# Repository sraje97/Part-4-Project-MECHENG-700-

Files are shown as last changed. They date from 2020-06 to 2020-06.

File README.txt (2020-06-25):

MECHENG700 - P4P
Eye-tracking System for Diagnosis of Visual Deficits
Author: S. Raje & J. Zhang

This contains all the MATLAB files used throughout the Part 4 project.
The files include:
	- On screen stimulus visualisation
	- Calibration Test
	- Fixation Tests
	- Trajectory Tests
	- Analyses for each test (Fourier analysis, Gaze position, Calibration, etc.)

The folder also includes a subfolder, "FINAL", of a few subject's results following the tests.

The final report and presentation are shown in the pdf and powerpoint slides respectively.

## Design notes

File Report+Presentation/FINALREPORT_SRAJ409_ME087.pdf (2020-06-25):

EYE-TRACKING SYSTEM FOR DIAGNOSIS OF VISUAL DEFICITS

### Sidhant Raje

Project Report ME087-2019

### RESEARCH PROJECT IN MECHATRONICS ENGINEERING

Co-worker: Jerry (Jia Jun) Zhang

Supervisor: Dr Luke Hallum

Department of Mechanical Engineering The University of Auckland

27 September 2019

ME087-2019

### EYE TRACKING SYSTEM FOR DIAGNOSIS OF VISUAL DEFICITS

### Sidhant Raje

### ABSTRACT

Millions of adults and children around the world suffer from visual deficits. When left untreated these visual deficits can cause severe vision loss and psychosocial issues [1]. This study pursues the design, build, and testing of an eye-tracking system for the diagnosis of strabismus, allowing for successful classifying and quantifying of strabismus.
The trials include a head mounted eye-tracker (the Jazz-novo), a CRT monitor, and dichroic filters (red and blue) for dichoptic presentation. Two sets of tests were carried out; firstly the 9-point fixation test, then the smooth pursuit tracking test. The visual stimuli was presented dichoptically such that at any one time, monocular perception was engaged whilst fixating or tracking. The stimuli was a circular, blue or red point which was only perceived through the right colour filter (blue for blue, red for red).
The fixation test stimulus oscillated 10 times (blue and red) with a frequency of 1 HZ at each of the nine locations on the grid. The tracking test stimulus travelled across both the horizontal and vertical meridians twice (once with blue stimulus and once with red stimulus). The tracking motion was a sinusoidal function, with a frequency of 0.12 Hz. Eight subjects participated in the formal trials of this experiment. Fast Fourier Transform (FFT) analyses were computed on the data from these subjects to acquire amplitudes, gains, and phases for the different sets of tests.
Results in this report outline two subjects who showed interesting results, one for fixation and one for tracking, and separate group analyses were also carried out. The results revealed distinct oscillations in the 1 Hz component of the eye-tracking data in either X or Y displacement for the fixation test. These amplitudes were compared relative to each subject’s calibration point and a relative gain was established for each subject. A larger gain meant larger magnitude of deviations which led to potential signs of strabismus. The tracking test results portrayed the gain and phase of the subject’s ability to track a moving stimuli. Higher gains meant there were overshoots from the relative gaze position, whilst lower gain corresponded to undershoots. Group results for the difference between Dominant Eye (DE) and Non-dominant Eye (NDE) gains and phases were also retrieved which revealed a possibility of diagnosing strabismus.
The results open an opportunity to diagnose and quantify strabismus with improving eye-tracking technology. These could one day lead to mobile eye-tracking systems in clinical practices for efficient use of time, resources, and introduce a level of autonomy.

ii

DECLARATION

Student

I hereby declare that:

1. This report is the result of the final year project work carried out by my project partner (see cover page) and I under the guidance of our supervisor (see cover page) in the 2019 academic year at the Department of Mechanical Engineering, Faculty of Engineering, University of Auckland.
2. This report is not the outcome of work done previously.
3. This report is not the outcome of work done in collaboration, except that with a potential project sponsor (if any) as stated in the text.
4. This report is not the same as any report, thesis, conference article or journal paper, or any other publication or unpublished work in any format.

In the case of a continuing project, please state clearly what has been developed during the project and what was available from previous year(s):

Signature:

Date:

Supervisor

I confirm that the project work undertaken by this student in the 2019 academic year is / is not (strikethrough as appropriate) part of a continuing project, components of which have been completed previously. Comments, if any:

Signature:

Date:

iii

### Table of Contents

iv

### List of Figures

Figure 1 | Four types of strabismic deviations | | 2
Figure 2 | Example of Prism-Cover test and the signs of esotropic strabismus . | 3
Figure 3 | Overview of eye-tracking system setup | | 6
Figure 4 | a) Chinrest and dichroic filter setup for subject. b) Subject performing
fixation test. c) Subject wearing the Jazz-novo eye-tracker | | 7
Figure 5 | Fixation and tracking test stimuli layout. a) 4-point calibration for
fixation test. b) Fixation test layout. c) Two 2-point calibration for tracking
test. d) Tracking test layout | | 9
Figure 6 | Subject testing procedure flow diagram | 10
Figure 7 | Data acquisition methodology | 11
Figure 8 | Subject A fixation test with filter placement RB. a) XY plot of the
9-point fixation test. b) X and Y displacement against time for fixation point 6. c) FFT analysis of X position at fixation point 6. d) FFT analysis
of Y position at fixation point 6 | 13
Figure 9 Overlay of normalised Y position for filter placements RB and BR at
fixation point 6 | 14
Figure 10 Fixation amplitude at 1 Hz over calibration amplitude at 1 Hz at the bottom-left corner of 9-point grid. a) Relative horizontal gain for all 8
subjects. b) Relative vertical gain for all 8 subjects | 15
Figure 11 Subject B tracking test response with filter placement RB. a) Horizontal tracking with left eye. b) Horizontal tracking with right eye. c)
Vertical tracking with left eye. d) Vertical tracking with right eye | 16
Figure 12 Polar plot of gain and phase for horizontal tracking. a) Dominant eye tracking. b) Non-dominant eye tracking. c) Difference between dominant
and non-dominant eye | 17
Figure 13 Polar plot of gain and phase for vertical tracking. a) Dominant eye tracking. b) Non-dominant eye tracking. c) Difference between dominant
and non-dominant eye | 18

### List of Tables

Table 1 | Subject information | 12
Table 2 | Subject B Gain and Phase at 0.12 Hz component | 16

v

### Acknowledgements

I would like to take this opportunity to thank the many people involved directly or indirectly with this project and those who have supported me in any way big or small throughout the year.
Firstly, I would like to thank my project partner, Jerry Zhang, for his consistent hard work and dedication to this research project. His passion for this research area kept me motivated throughout the year and contributed greatly to the success of this project. I could not have asked for a better peer to work alongside with.
I would like to thank our supervisor, Dr. Luke Hallum, for going above and beyond with his continuous support and guidance. His expertise and advice always came in handy whenever we hit a roadblock and his feedback throughout the various stages of this project are greatly appreciated. He has inspired me to follow this field of research in my forthcoming years.
I would also like to thank Lucy Yan for her support throughout the year. She has always been there to talk to for any of our hurdles and provided excellent ideas and solutions to overcome them.
Finally, I would like to thank our friends, family, and peers who dedicated their precious time for our experimental trials. There efforts are acknowledged and contributed greatly to the success of this project.

vi

### Glossary of Terms

Visual Deficit | Visual impairments leading to decreased vision
Eye Tracking | Measurements denoting the horizontal and vertical positions of
| a subject’s gaze
Dichoptic Presentation Presenting a stimulus to one eye at a time
Monocular Perception Seeing the visual stimulus through a single eye
Binocular Perception Seeing the visual stimulus via both eyes simultaneously

### Abbreviations

VA | Visual Acuity
ADC | Analogue to Digital Converter
FFT | Fast Fourier Transform
DE | Dominant Eye
NDE | Non-dominant Eye

vii

### 1. Introduction

Millions of adults and children around the world suffer from visual deficits. When left untreated these can cause severe vision loss and psychosocial issues [1]. Adverse psychosocial effects consist of problems in childhood and education, job prospects, interaction with peers, may manifest more seriously as psychiatric disorders, and may also be detrimental to the general quality of life [2]. According to the American Academy of Pediatrics, early diagnosis and intervention is necessary in preschool and early childhood to reduce these risks by more than 50%, by the age of 7. Children with first-degree relatives with similar conditions should also be referred to testings early on [3].
There are many shortcomings to the manual visual diagnostic methods currently in use. Majority of the current visual diagnostic methods require a professional or specialist to conduct the vision screening tests. These are manual and lack quantitative measures. They use resources and time from the facility as well as the patients, making them expensive and undesirable. Furthermore, the conducting of the screening tests is often difficult and subjective, and predominantly requires communication between the patient and ophthalmologist. This can lead to a communication barrier with young or non-verbal children. In these cases specifically, observational methods are favourable and should be conducted. Eye-tracking is a non-invasive method currently used for detecting visual abnormalities in patients. Eye-tracking is a relatively new area of research but becoming increasingly popular as technology advancements occur with cheaper, more reliable eye-trackers being more readily available - thanks to the gaming industry. These new devices can slowly minimise the subjectivity of tests and bring in more accurate measurements. There are multiple areas in life where research is being done using eye-tracking devices including; medical research, marketing and social applications, education, and gaming/VR [4]. In this paper, we focus on the medical research and usage of eye-trackers; specifically, the diagnosis of visual deficits using an eye-tracking system.
We propose to develop a test for diagnosing strabismus using eye-tracking. Our test must, for the most part, be automatic and objective when detecting strabismus in subjects. We will acquire gaze position using fixation points for the subject to observe on screen, and a set of horizontal and vertical traversals to track. Through our trials and testing, the data gathered and analysed should give us a better understanding of visual acuity in strabismic subjects and potentially lead to developing a quick-and-easy, mobile system for use by ophthalmologists or paediatricians in visual screening tests.

### 2. Literature Review

### 2.1 Visual Deficits

There are a number of visual deficits which affect visual acuity and many of these can have potentially adverse effects on the patient. Strabismus is one of the most commonly diagnosed visual abnormalities which could lead to visual deficits. Fortunately, treatment of strabismus has high success rate if treated early. Therefore, we are focusing our study on diagnosing patients with strabismus.
Adult strabismus is present in approximately 4% of the adult population [2,3,5]. Strabismus, sometimes known as squint or heterotropia, is the irregular alignment of one (or in rare cases, both) of the visual axes of the eye; a measurable relative deviation between the visual axes is thus observed. This abnormality is caused by weakened motor fusion mechanism or neuromuscular anomalies in the eye [6].
There are two classifications of strabismus; comitant and incomitant. The former resulting in deviation within physiological limits and same in all directions of gaze. Whilst in the case of the latter, the extraocular muscles show signs of paralysis and hence the magnitude of deviation varies at different directions of gaze [6]. There are also four types of strabismic deviations in the eye, as shown in Figure 1 and explained below:
- Esotropia - Horizontal convergence (inwards displacement) of visual axis
- Exotropia - Horizontal divergence (outwards displacement) of visual axis
- Hypertropia - Vertical upwards displacement of visual axis
- Hypotropia - Vertical downwards displacement of visual axis

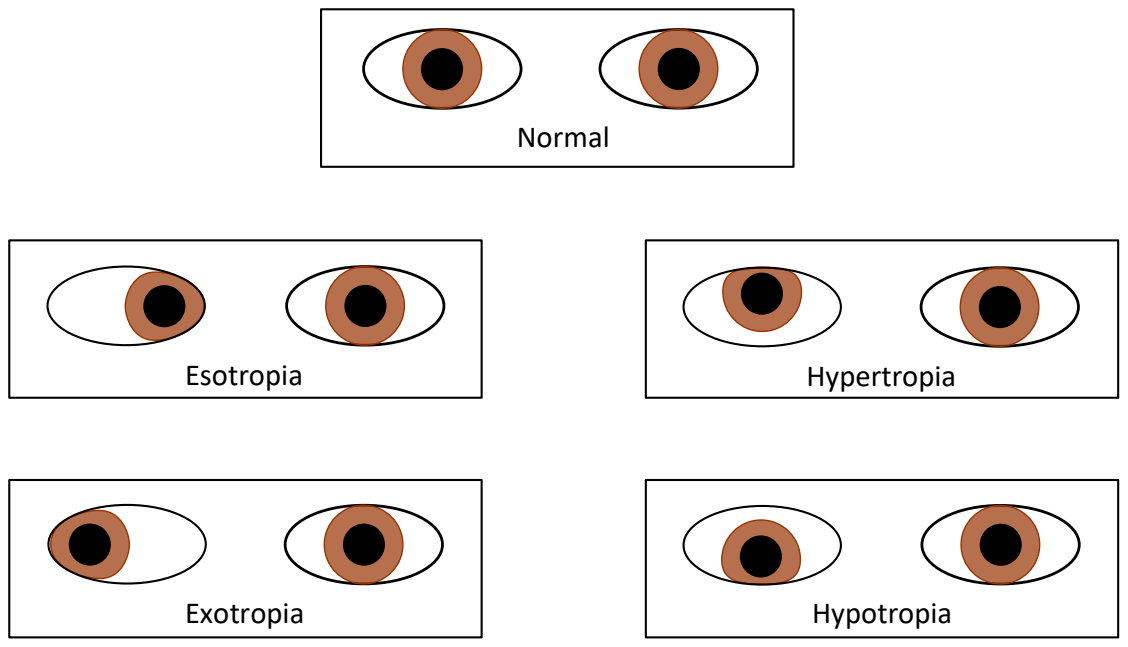
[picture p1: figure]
Normal; Hypertropia; Exotropia; Hypotropia; Esotropia

Figure 1 Four types of strabismic deviations

Those who acquire ocular misalignment as adults usually report diplopia (double vision) and visual confusion. When strabismus occurs earlier, in childhood, these symptoms are absent as the visual system learns to suppress images from the deviated eye when viewing binocularly [7]. However, untreated strabismus has still been found to lead to amblyopia (decreased vision), weakened three-dimensional perception [5], as well as the psychosocial effects mentioned earlier - problems in education and job prospects, interaction with peers, and detrimental to general quality of life. Therefore, early diagnosis and treatment is vital. It has shown to provide improved outcomes and prevent the degradation of visual acuity and other aforementioned problems. This is why there is a key focus on diagnosis of strabismus in our research.

### 2.2 Current Test Methods

2.2.1 Eye Movements (Smooth Pursuits/Saccades)
Part of the eye-tracking method is to design and implement gaze tracking of the eyes when following a target point. In target tracking there are two forms of movements of the eyes, smooth pursuit and saccadic eye movement. Smooth pursuit is the gradual tracking of a target to keep the target on the fovea, where speeds of the observed moving object are less than 30°/s with reference to the observing eye. Saccadic movements are short and fast transitions of the eye from one viewpoint to another, and generally occur above the mentioned speed. A [saccadic] latency of 100-200 ms can also be expected to ‘catch up’ to the moving target [8].

2.2.2 Manual Tests
Manual tests carried out by ophthalmologists are laborious and time consuming. These tests include the Cover-Uncover test, Prism and Cover test, and Maddox Cross test, and others [6]. They require equipment such as occluders, prisms, filters and other apparatuses which are brought close to the face and eyes of the subject - requiring a high level of trust between patient and clinician. This would cause unrest in many young children or those with other behavioural issues. The tests require input from the subject and/or clinician in order to correctly test and diagnose signs of strabismus - making them highly subjective. Most of these tests also lack quantitative and accurate measures of deviation (other than the Maddox Cross test) which we hope to overcome using our system. An example of the Prism-Cover test is shown in Figure 2. Depicting how the prism and occluder are used conjointly to detect signs of strabismus in an esotropic subject.

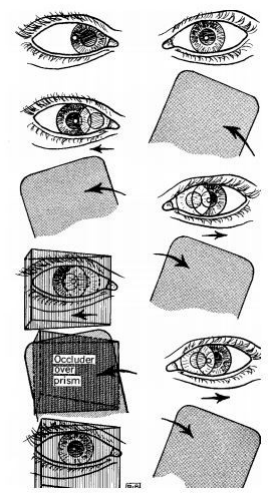
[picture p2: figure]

Figure 2 Example of Prism-Cover test and the signs of esotropic strabismus

2.2.3 Eye-tracking Tests
Eye-tracking during fixation tasks has recently been used to quantify visual deficits. Using a 9-point grid of fixation points equally spaced across the screen, similar to that used by ophthalmologists, subjects carried out a digitised eye-tracking test. In the paper by Hafed et al. [9], a 9-point fixation test was conducted with blind patients - with subretinal visual implants - using eye-tracking. Similarly, in the paper by Chen et al. [5], the researchers used a Tobii X2-60 connected to a laptop for an eye-tracking system, with the subject seated 50 cm away. Using their Tobii eye tracker, they retrieved X and Y coordinates of each eye and hence determined the Euclidean distances between a gaze pair and the fixation point. Using these Euclidean distances, four weighting coefficients, and a bias, they computed the strabismus occurence feature, fso. If fso was greater than 0 than the subject was deemed to be strabismic, whilst 0 and lower meant subject was visually normal. They observed in strabismic subjects that one eye has a gaze point close to the target whilst the other eye (the strabismic eye) is, relatively, further away. They also observed on certain points on the screen, the strabismic subject could fixate precisely whereas for points in other directions the gaze data did not align as well. This can be explained by the case of incomitant strabismus. Their results from the data analysis was accurate in diagnosing strabismus, as they correctly classified strabismic and visually normal subjects. This is an important leap forward in this area of research as they were able to objectively, and with minimum input from subject or clinician, predict strabismus in the subject.
Eye-tracking has also been used in tracking tasks to detect strabismus. In the paper, “Strabismus Screening by Eye Tracker and Games” [10], the researchers used a Gazepoint GP3 Desktop Eye Tracker connected to a desktop monitor with the subject 33 cm from the eye-tracker. On the screen were 5 points, in the shape of a ‘plus sign’, and the subject was to follow a series of tasks which required traversing multiple times from top to bottom, then traversing from left to right of the screen. This was done to simulate smooth pursuit of the eye’s motion. They retrieved gaze data of each eye and determined the Euclidean distance and compute a threshold distance which they would use to predict strabismus (similar to the last study). An Euclidean distance threshold, Dthreshold ≥ 0.05, was considered as the limit for determining the subject as strabismic. Their predictions were all accurate in determining their controlled visually normal group, and the strabismic patients’ group, totalling 50 subjects.
We propose to confirm and extend the results described above, by Chen et al. [5] and Saisara et al. [10], by measuring both fixation and smooth pursuit in visually normal and strabismic subjects. Using a similar fixation test in conjunction with a smooth pursuit tracking test, gaze point data will be gathered from the subject. We hope to observe changes in the average gaze points of the eyes when tracking a point horizontally, and similarly with vertical tracking. This could potentially aide us in detecting strabismus through the deviation of the eyes, as they had done, in quantifying the amount of deviation in the strabismic eye, and potentially the classification of the strabismus; comitant or incomitant.

2.2.4 Stimulus Shape
An inappropriate stimulus presented can introduce unwanted saccades or microsaccades during testing. It is critical to present stimulus with minimal bias towards these saccadic motions. Hafed et al. [9] reasoned that shapes with larger horizontal dimensions (rectangle) introduced predominantly horizontal saccades. Therefore, an equilateral shape such as a circle, with no hard edges, should be used to present stimuli.

### 2.3 Eye-tracking Devices

There are multiple eye-tracking devices on the market many of which provide adequate data in numerous areas of research. They can also be crossed into medical research as required in our study. We had two devices available to us, the Tobii Eye Tracker 4C and the Jazz-novo SN 1060.

2.3.1 Tobii Eye Tracker 4C
The Tobii Eye Tracker 4C is a plug-and-play device which is compatible with Windows 7 and above. Originally intended for gaming purposes, the Tobii allows the user to perceive their gaze on their screen and is a useful tool for use with assistive gaming features (with compatible games only). The Tobii Eye Tracker 4C is a USB (2.0) powered device which can be mounted on top of a monitor or connected to a laptop. It uses two near-infrared illuminators to track the eyes at an operational frequency of 90 Hz [11]. Setup is straightforward and requires the company’s proprietary software for calibration (during setup and initialisation) and use, but a separate SDK and license is required for acquiring gaze point data - used by researchers and developers.
A similar eye-tracker from Tobii, the Tobii Pro TX300, was used in a study conducted at the University of Melbourne [12]. The objective of the study was on nystagmus identification using the acquired gaze data. The results indicated that it is possible to distinguish between congenital (developed in infancy) and acquired (developed later through illness/brain dam-age) nystagmus through the gaze data alone, and other observations in eye movement in the subject were also made which are not easily seen using manual testing procedures. This is a clear advantage of eye-tracking, over manual tests, that has not been available until recent developments in eye-tracking technology. However, a downfall of this, and the Tobii Eye Tracker 4C, is that monocular calibration is not possible, meaning that the ability to alternate occlusion (obstruction of sight to single eye) with an occluder (or similar filter) is not possible for gaze data purposes. Real-time monitoring of the eye positions is also not possible, meaning the gaze analysis must be processed after the screening phase and not in-situ.

2.3.2 Jazz-novo SN 1060
The Jazz-novo SN 1060 is a head mounted eye-tracking device developed primarily for pilots to collect information of their interaction with the cockpit of the plane. Designed and built by Polish company, Ober Consulting, this device measures vertical and horizontal eye movements (1000 Hz), head rotation and acceleration in both axes (1000 Hz), pho-toplethysmographic signals (heartbeat and relative changes in blood oxygenation) (500 Hz), and audio signals (8 kHz) [13]. The setup for this requires a BioSemi data acquisition set and the corresponding LabVIEW data acquisition software, ActiveView, which is compatible with Windows, Mac, and Linux machines. The Jazz-novo does not provide individual tracking of the eyes, instead it provides the averaged deviation of the two eyes by illumin-ating the inner canthi and pupils with low intensity IR light [13]. This leads us to having to come up with another solution to tackle our research problem. To overcome this a pair of coloured dichoptic filters are placed in between the screen and the subject’s two eyes to suspend vision of the target point in one eye, this is explained in detail in Section 2.4.

### 2.4 Dichoptic Stimulus Presentation

Dichroic filters can be used to present different stimuli to each eye. They can allow monocular presentation to one eye whilst suppression of an image to the other eye. This was trialled in the paper by Economides et al. [7], where subjects wore specialised glasses containing dichroic filters; red for the right eye and blue for the left eye. The red filter was highpass and blue filter was lowpass, with cutoff frequencies at 600 and 501 nm, respectively. The stimuli shown on screen were either red, blue or purple dots on a greyish-purple textured background. The purple textured background meant that ‘cross-talk’ between stimuli presented would be minimised, such that complete suppression occurred in the eye with the opposite filter colour as the stimulus colour (i.e. red filter and blue stimulus would be suppressed in the right eye). The trials done in this paper showed whilst strabismic subjects fixated one eye centrally on the screen (at a crosshair) through dichoptic stimulus presentation, they were still able to correctly recognise a stimulus in the peripheral vision majority of the times. A similar technique can also be used in our eye-tracking system to present red and blue stimulus at the nine different fixation points, as well as for the tracking tests. This would help in quantifying fixating and tracking performance of each individual eye given the resultant gaze position from the eye-tracker.

### 2.5 Conclusion of Literature

Early diagnosis and treatment of visual deficits is vital to prevent adverse physical and psychosocial effects on the patient [1, 2, 5]. Strabismus is an exceedingly common visual deficit [3]. We propose to develop an improved test for strabismus; our set up may also yield basic insight into the characteristics of this visual disorder. An eye-tracking system decreases subjectivity and reduces the manual methodology - as seen in the studies by Chen et al. [5], and Saisara et al. [10]. This brings upon an accurate and cost-/time-efficient solution for visual screening tests for the patient as well as the ophthalmologist. Our proposed method would consist of an adaptation of both methodologies presented, as well as include the dichoptic presentation technique for suppression of visual stimulus to a specified eye. A combination of the fixation and tracking tests would help in the diagnosis of strabismus, and classifications of strabismus in subjects. Potentially, this technology could help open a doorway into faster, more mobile solutions for visual screening in clinical practice.

### 3. Experimental Design

### 3.1 Equipment Setup

The eye-tracker used for gaze-point acquisition was the Jazz-novo SN 1060 [13]. Worn on the subject’s forehead, the eye-tracker used Direct Infrared Oculography to provide gaze position data in terms of X and Y positions. The sampling rate of the eye-tracker was 1 kHz with eye position readings given in arbitrary units (a.u.), corresponding to relative pupil deviation from the inner canthi. The horizontal measurements and vertical measurements ranged between ±35° and ±20°, respectively. The X and Y positions were the resultant (averaged) horizontal and vertical displacements of both eyes; not a pair of individual eye-tracking measurements. This led to some slight alterations in our experimental design such as introducing the dichroic filters in the test and conducting the fixation and tracking tests twice (with filters swapped). The Jazz-novo also connected to the BioSemi Active Two Data Acquisition unit via an optical cable for data acquisition. Which connected to a second laptop to acquire data using the BioSemi ActiView software [14] as a BDF file.

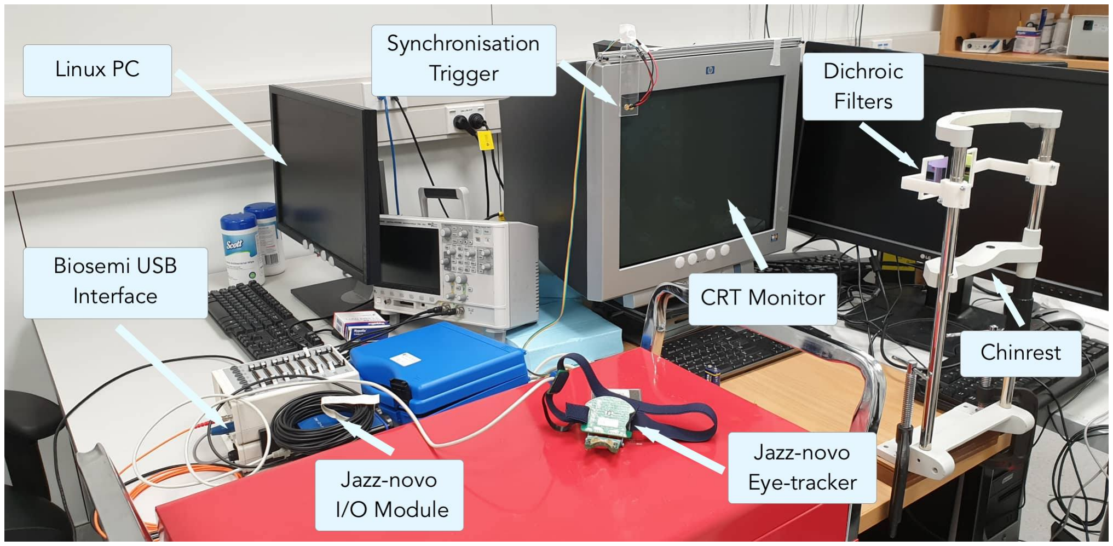
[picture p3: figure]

Figure 3 Overview of eye-tracking system setup

The test stimuli were shown on a Cathode Ray Tube (CRT) monitor running on a Linux system - placed 50 cm away from the subject. The screen resolution was fixed at 1152 x 864 pixels and screen refresh rate at 75 Hz. Two photodiodes were fixed at the top left-hand side of the monitor to detect the pulsation of a white square. This white square pulsation was designed as a trigger point for the commencing of different events, such as the start of calibration points, fixation points, and smooth pursuit tasks. The photodiodes connected to an Arduino Uno, which read the ADC value and output a digital ‘High’ when a white square (ADC ≥ 1000) was detected. This allowed for time synchronisation of data points to the test events later during analysis. A chin rest was used to ensure the distance from the monitor was kept constant for all subjects and to prevent head movement during the course of the screening tests.
A pair of dichroic filters (blue and red) were also fixed in front of the subject’s eyes; slotted within a 3D printed mount. These 50 x 50 mm filters allowed transmission of a narrow wavelength of light to pass through, whilst reflecting others from the visible spectra. The blue filter’s transmittable wavelength range was 465-525 nm, whilst the red filter’s transmittable wavelength range was 600-680 nm. Due to the high level of reflection from dichroic filters, the lights in the room were switched off during the tests to allow subjects to focus on the stimuli presented. The experimental setups are shown in Figure 3
and Figure 4.

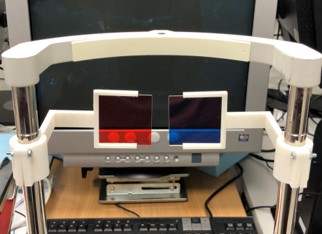
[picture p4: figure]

(a)

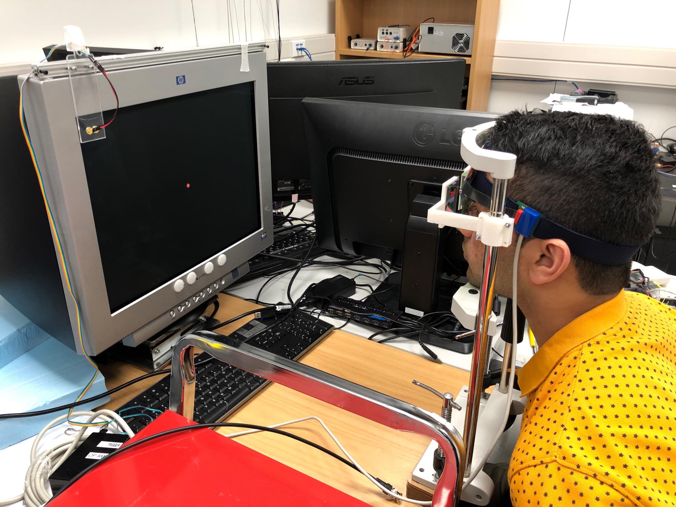
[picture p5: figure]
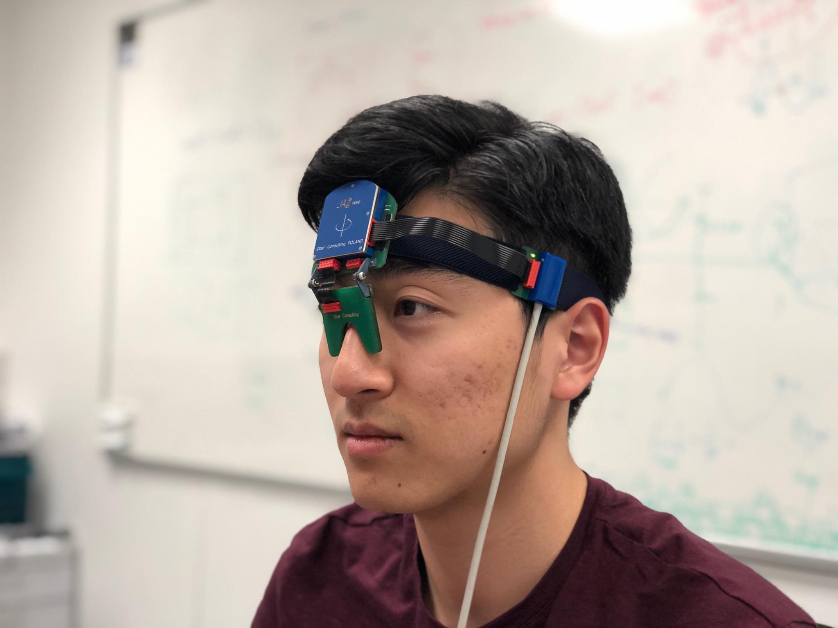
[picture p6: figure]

(b) (c)

Figure 4 a) Chinrest and dichroic filter setup for subject. b) Subject performing fixation test. c) Subject wearing the Jazz-novo eye-tracker.

### 3.2 Eye-tracking Tests

Concluding the literature review, having revealed fixation and tracking tests are both great measures of a subject’s visual ability - there were two sets of tests planned for the subject to undertake. First, the 9-point fixation test - a grid of nine points equally spaced across the computer monitor. Second, the tracking test - a stimulus moved back and forth along the horizontal meridian, or the vertical meridian. In both cases, the displacement of the stimulus against time was sinusoidal. These tests were created using MATLAB and the Psychtoolbox-3 [15] packages which are available as an open-source resource for vision and neuroscience research. The tests were simple and required minimal effort from subjects allowing them to be effective on all ranges of subjects, including children.

3.2.1 Fixation Test
The fixation test consisted of a set of four calibration points and a set of nine fixation points, both made of 10-pixel wide circles. The calibration points were arranged in a grid formation such that they formed the perimeter of a square. The colour of these calibration points were white so that both eyes were able to perceive the stimuli (past the filters) and the subject would fixate normally using binocular perception. The points were displayed one after another for a period of three seconds each; starting from top right, then bottom right, bottom left, and eventually top left - order is shown in Figure 5a. These four segments allowed visualisation of the subject’s relative gaze position on the screen as well as calculation of the resolution coefficient, C. The resolution coefficient enabled us to convert measurements from arbitrary units to units of mm, for both horizontal and vertical meridians. These values were acquired by finding the difference between the top and bottom calibration points for vertical, and the difference between left and right calibration points for horizontal. Then, dividing by the physical length of the grid in screen space -195 mm for both.
The fixation test consisted of nine stimulus locations. At each location, the stimulus alternated between red and blue at a rate of 1 Hz. The order of the stimulus being presented is shown in Figure 5b - starting at top left and working around the grid in the shape of the digit ‘2’ such that minimal effort was required between transitions of fixation point locations. The nine points were equally spaced at a distance of 288 pixels (≈ 50 mm) vertically and horizontally from each other, such that the various points were easily distinguishable from each other in the acquired data. The total duration of the test was 111 seconds with a break in between so that the subject’s eyes did not incur excess stress which could have led to poorer fixating performance. From the fixation tests we aim to see relatively large oscillations in gaze position for a subject with misalignment in the visual axis when fixating alternation between blue and red stimuli, at 1 Hz.

3.2.2 Tracking Test
Tracking tests consisted of two sets of horizontal and two sets of vertical smooth pursuit tasks; each with blue or red stimuli. The tracking tests also required calibration points before commencing the smooth pursuit tasks to quantify relative screen gaze positions. The first set of calibration points were displayed at the left and right locations on the screen (indicated by the points labelled ‘1’ in Figure 5c). Then the tracking of a blue stimulus began which travelled from left to right twice, followed by a red stimulus with an identical path; as shown in Figure 5d. Models of these paths were created using a phase shifted sin function,
Xposition = a sin(2πf + φ) | (1)

where a is the amplitude or distance from centre to the point horizontally (in pixels), f the frequency or speed of the moving target, and φ the phase shift to start the target tracking from the left position.
Similarly, the second set of calibration points were displayed at the top and bottom locations on screen (indicated by the points labelled ‘2’ in Figure 5c) before commencing the vertical smooth pursuit. These calibration points were followed by a set of blue then red vertically moving targets between the top and bottom grid points. The path modelled for the blue and red stimuli were similar in nature to Equation 1 but with output as Y pixel position for vertical motion, rather than X.

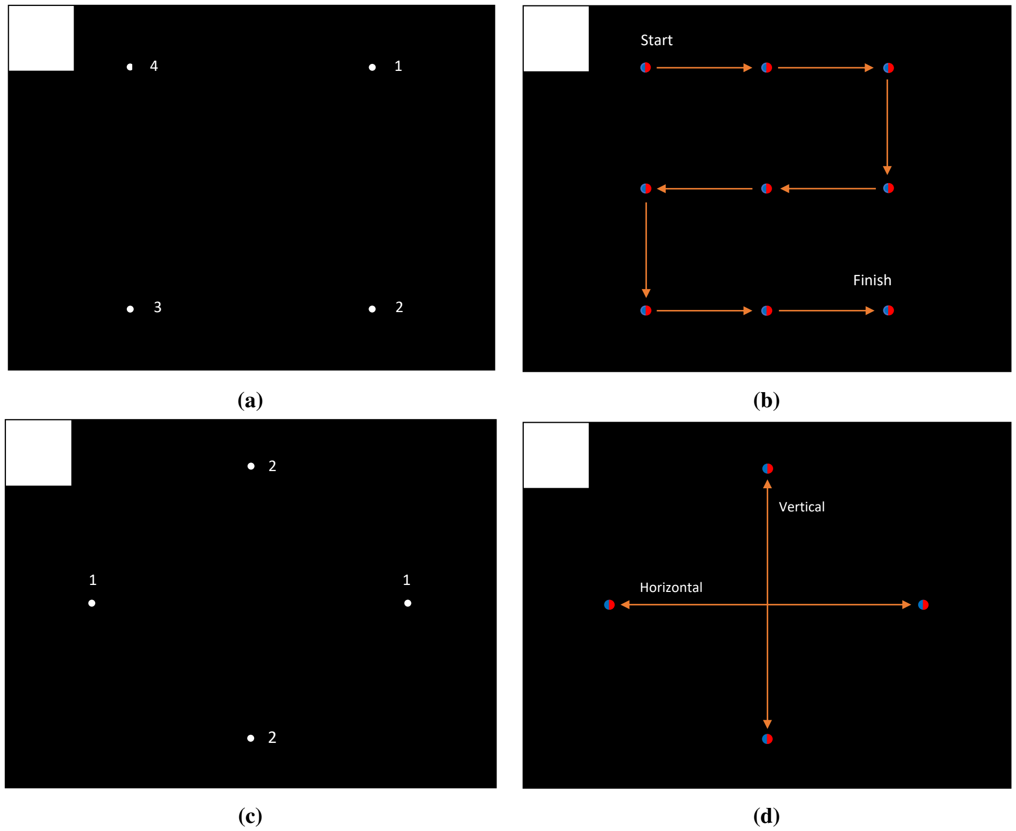
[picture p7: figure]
Start; Finish; Horizontal; Vertical

Figure 5 Fixation and tracking test stimuli layout. a) 4-point calibration for fixation test. b) Fixation test layout. c) Two 2-point calibration for tracking test. d) Tracking test layout

The frequency of the modelled sine wave was constant at 0.12 Hz, meaning the total duration of two cycles was 16.67 seconds for each smooth pursuit task. The total duration for the tracking tests was ≈ 105 seconds - combining smooth pursuit segments and the breaks in between these segments. The speed of the smooth pursuit segment was designed such that saccadic eye movements would not occur - velocity of stimuli less than 30°/s. The actual speed was less than 10°/s at max velocity (in the centre).
Due to the nature of the Jazz-novo eye-tracker, acquiring individual eye gaze points was not possible, hence, a workaround solution using the dichroic filters was implemented. Applying the phenomenon of dichoptic presentation, the filters were used such that only a single eye was being engaged at a time. The stimulus colour was adjusted to the correct intensity such that it was perceivable by the subject by the corresponding filter (i.e. red colour - red filter), and completely occluded by the opposite. This enabled us to simulate individual eye-tracking by allowing only one eye to fixate and correctly assume the resultant X and Y positions corresponded to that single fixating eye.

### 3.3 Subject Testing

3.3.1 Testing Procedure
Multiple volunteers took part in initial testing of the system and eight subjects participated in the formal trials for analysis. All volunteers reported they were visually normal - in the sense that they did not have known strabismus. Some subjects were regular users of prescription glasses but weren’t able to wear them on top of the Jazz-novo. However, the subjects reported they could clearly distinguish the red and blue presented stimuli hence their fixating/tracking performance was not biased.
Subjects were tested in the Brain-Computer Interface (BCI) Lab at the University of Auckland with the experimental setup described previously. Subjects provided written, informed consent to the acquisition of their eye-tracking data, and for their results to be published in this report (and other media). Each subject was required to do four sets of eye-tracking tests with filters swapped - two fixation tests and two tracking tests. Subjects were told instructions prior to testing the process of each test; including the calibration points and rest breaks. The first test was the fixation test with the red filter on the left and blue filter on the right (filter placement RB). After finishing, the filters were swapped (filter placement BR), and the same fixation test carried out again in order to reduce any bias relating to a single eye - from having greater colour perception (i.e. can see red brighter). Then, the tracking test was carried out with the same filter placement, BR. Finally, the filters were swapped back to their original RB placement and the tracking test was carried out again. The process diagram is shown below in Figure 6.

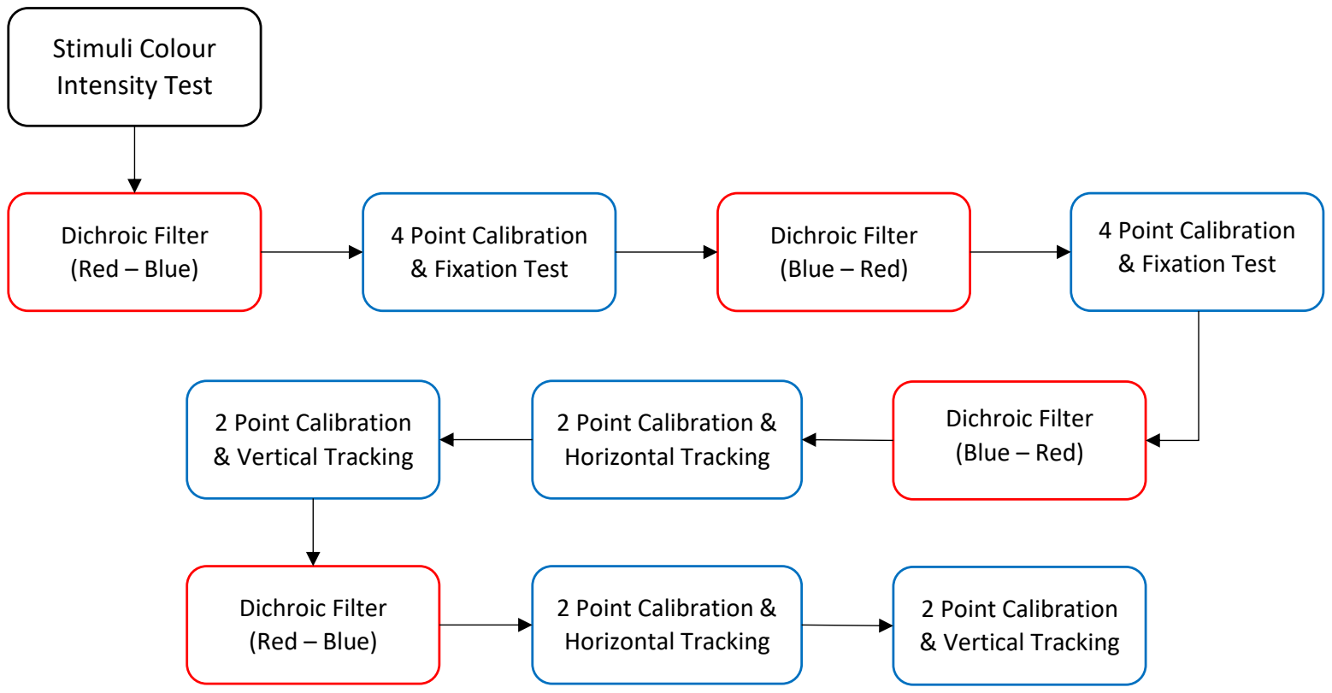
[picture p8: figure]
Stimuli Colour Intensity Test; Dichroic Filter (Red – Blue); 4 Point Calibration & Fixation Test; Dichroic Filter (Blue – Red); 2 Point Calibration & Horizontal Tracking; 2 Point Calibration & Vertical Tracking

Figure 6 Subject testing procedure flow diagram

During testing, caution had to be taken to get the appropriate luminosity of the stimuli for each subject as the red generally had some ‘cross-talk’ through the blue filter. This meant a faint shadow of the red stimuli was perceived through the blue filter if the stimulus was too bright. To overcome this, before formal testing, a red and blue stimuli were presented at the centre of the screen and subjects were asked to observe both colours through each filter to determine if any transmission was observed in the incorrect filter. If so, the intensity (0 - 255) was decreased until the ‘cross-talk’ was unnoticeable. Most subjects required an intensity of 40% for the red stimulus, and 50% for the blue stimulus.

### 4. Data Processing

### 4.1 Data Acquisition

Acquiring data from the Jazz-novo eye-tracker required substantial software setup. Three different sets of software and toolboxes were required to acquire and display the gaze point data; BioSemi ActiView, FieldTrip Toolbox, and MATLAB.
The Jazz-novo was connected to the BioSemi Active Two Data Acquisition unit which exclusively worked with the BioSemi ActiView software. This proprietary software, also developed by BioSemi, was used to generate the ‘.BDF’ file type, which was not a common software file type. Hence, a MATLAB toolbox - the Fieldtrip toolbox [16] - was installed to decipher the saved ‘.BDF’ file. The toolbox contains a range of functions for the acquired data by reading the ‘BDF header’ and the specified signal channels in the file. For this study, only the ‘EyeX’ (X Position), ‘EyeY’ (Y Position), and the ‘Status’ (Trigger) channels were of importance. These were saved to MATLAB variables - ‘rawX’, ‘rawY’, and ‘trig’ - to be accessed during data analysis. The data flow diagram is shown below in
Figure 7.

Jazz Novo SN 1060

Biosemi ActiveTwo

BDF File

MATLAB – (Fieldtrip)

X-Y Pos. & Trigger data

Data Analysis

Laptop (ActiView)

Figure 7 Data acquisition methodology

### 4.2 Data Filtering and Segmentation

The BioSemi Active Two sampled at a frequency (2048 Hz) more than double that of the Jazz-novo eye-tracker (1000 Hz). This meant that the Nyquist criterion was met and subsequently, every even indexed value was an exact replica of the previous value. Hence, the acquired raw data was filtered such that these copies were deleted. Once filtered, the data were segmented into the respective 3 second long calibration segments, and fixation or tracking segments. Fixation segments comprised of 8 seconds worth of data at each of the nine points. Although the fixation at each point lasted 10 seconds, the beginning and ending one second worth of data points were deleted to eliminate any early anticipation the subject may have performed from switching too soon. Tracking data were left at their entire 16.7 seconds long segments because anticipation could be ruled out; the subject simply had to follow the stimuli.

### 5. Results and Discussion

Data from fixation and tracking tests were analysed and reviewed independently for each subject. This analysis was done by applying the Fast Fourier Transform (FFT) method to individual subject’s segmented data. The analyses revealed the amplitudes at 1 Hz frequency for the different fixation points, and the gain and phase of tracking performance from the tracking tests. Relevant information of each of the eight subjects in the formal trials are presented below in TABLE 1.

Table 1 Subject information
Subject | Sex | Known Presence of Strabismus | Dominant Eye | Eye Colour
A B C D E F G H | Male Female Male Male Male Male Female Female | No No No No No No No No | Right Right Right Right Left Right Right Right | Blue Brown Blue Green Brown Brown Brown Brown

### 5.1 Fixation Test

5.1.1 Subject A Results
The 9-point fixation test was the first screening test to be performed. Amongst the group, Subject A had interesting results overall in their fixation data so their respective plots are presented in Figure 8. The top-left plot, Figure 8a, shows all nine fixation points for Subject A with filter placement RB (red filter on left, blue filter on right). This plot shows the X against Y position for the eight second long segmented fixation data. As can be seen, the clusters on the left and right side have greater spread than those in the centre, indicating that the subject had higher magnitude in oscillations and deviated their eyes further to re-fixate on the points at the sides, compared to the centre section.
These oscillations can be seen distinctly in Figure 8b. The plot of X and Y displacement against time expresses fixation point 6 (middle-left point of grid) as there were significant amounts of horizontal and vertical oscillations present. Using FFT, this fixation point was analysed to retrieve the oscillation amplitude at the 1 Hz component - the frequency at which the blue and red stimuli were oscillating. These FFT plots are shown in Figure 8c for X oscillation and in Figure 8d for Y oscillation, for both filter placements RB and BR. The 1 Hz component of the FFT revealed that Subject A was alternating fixation. Subject A is a visually normal subject but the pattern of results suggests they may show signs of incomitant strabismus - signs of visual paralysis in different gaze directions [6]. Comparing Subject A’s amplitudes of X and Y oscillations; the two 1 Hz component peaks for X with

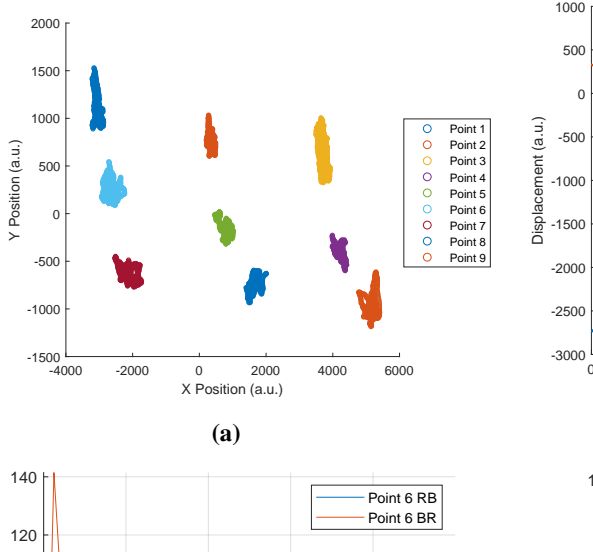
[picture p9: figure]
X Position (a.u.); Y Position (a.u.); Point 1 Point 2 Point 3 Point 4 Point 5 Point 6 Point 7 Point 8 Point 9; Displacement (a.u.); Point 6 RB Point 6 BR

0 | 1 | 2 | 3 | 4 | 5 | 6 | 7 | 8
| | | | Time (s)

X Position
Y Position

(b)

0 | 1 | 2 | 3 | 4
Frequency Component (Hz)

0

20

40

60

80

100
Amplitude (a.u.)

(c)

0 | 1 | 2 | 3 | 4
Frequency Component (Hz)

0

50

100

150

Amplitude (a.u.)

Point 6 RB
Point 6 BR

(d)

Figure 8 Subject A fixation test with filter placement RB. a) XY plot of the 9-point fixation test. b) X and Y displacement against time for fixation point 6. c) FFT analysis of X position at fixation point 6. d) FFT analysis of Y position at fixation point 6.

filter placement RB (62 a.u.) and BR (78 a.u.), are relatively lower than those for Y with filter placement RB (92 a.u.) and BR (158 a.u.). This suggests that whilst gazing towards the left, Subject A had greater magnitude of deviation vertically in their visual axes. This could also indicate the subject had a greater level of hypo/hyper-tropic strabismus rather than eso/exo-tropic.
The amount of deviation of the eye could also be quantified using the amplitude of these 1 Hz peaks. The deviation is equivalent to the amplitude of the oscillation during fixation, in units of millimetres. Realising the deviation required computing the difference between the fixation and calibration amplitudes at 1 Hz, with respect to the resolution coefficient, as described in the following equation

Deviation =

A1
C

−

A0
C

(2)

where A1 = fixation point amplitude at 1 Hz, A0 = calibration point amplitude at 1 Hz, C = resolution coefficient (a.u./mm), and Deviation = deviation noticed on screen (mm). The
deviation could be considered for both horizontal and vertical deviations. For Subject A it was approximated that the horizontal deviation was 1.00 mm, and the vertical deviation was 6.12 mm. These were the average values from both RB and BR filter placements.

Plausibility of these deviations need to be confirmed. To confirm the accuracy and precision of these deviation values, multiple trials on the same subject could be conducted to observe if there is minimal variability within trials, in the future. Averaged deviation values across all nine points could also be taken into consideration. Nonetheless, this analysis does acknowledge the fact that these vertical (or horizontal) oscillations can potentially be used to classify the type, and quantify the severity of strabismus a subject may have.
Similar analyses were carried out with the other test subjects who did not show significant peaks at the 1 Hz component, as subject A did in the Y direction. Subject B had a few distinct peaks whilst most other subjects showed relatively weaker peaks in the X FFT analysis. Peaks observed at the 0.125 Hz component throughout all FFT plots were disregarded, as these were introduced when processing the data into the eight second segments. They were not a true reflection of the subject’s fixation performance. Observing the phase difference between the eyes with both filter placements enables us to check the subject is consistent in their performance and was not unduly biased due to having greater colour perception in one eye. The phase difference plot is illustrated in Figure 9 - for fixation point 6 with both filter placements RB and BR. In the plot, it appears that the peaks for BR predominantly align with the troughs for RB, and vice versa. This indicates they may be 180° out of phase. Analysis from FFT confirms that at the 1 Hz component, the phase difference is 202°. This indicates that the subject alternated fixation by moving their eyes up for one set, and down at the exact same time stamp with the other filter placement. Thus their performance can be concluded to be unbiased due to effects of the colours. This is consistent with the results of dichoptic presentation (and occlusion) realised through the filters trialled in [7].

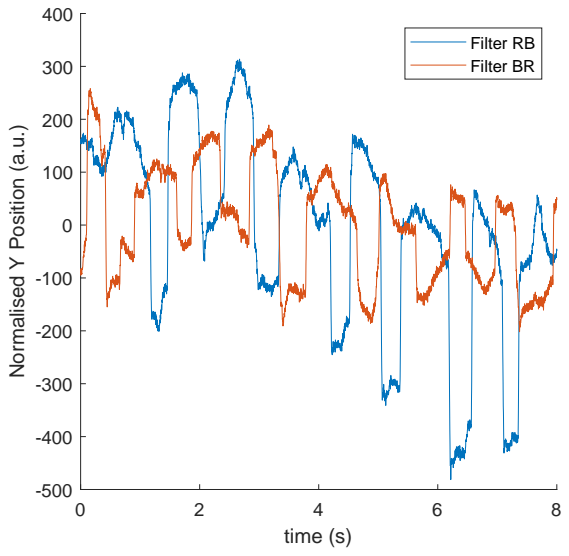
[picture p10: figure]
time (s); Normalised Y Position (a.u.); Filter RB Filter BR

Figure 9 Overlay of normalised Y position for filter placements RB and BR at fixation point 6

5.1.2 Group Results
Vertical or horizontal oscillation may be observed in strabismic patients when occlusion of a single eye is alternated [6]. This is the basis of the manual method of cover test and the adapted, eye-tracking fixation test in our study. The X and Y displacement oscillations are plotted for all eight subjects in Figure 10 which show the magnitudes of oscillation at fixation point 6 relative to the subject’s nearest non-oscillating calibration point, point 3.

As expected a visually normal subject would see little to no oscillations, thus, most subjects’ gains are spread around 1. The significantly high gain of Subject B in Figure 10a represents high magnitudes of X oscillation at this location which could be expressing symptoms of eso/exo-tropic strabismus. Similarly, the vertical oscillations in Y were only apparent in Subject A, which explains their higher gain amongst the group of test subjects. However, the short segment of calibration (three seconds) with large frequency bins could have an affect on the accuracy of the true 1 Hz amplitude for calibration points. A larger segment of data could have been acquired to help improve this issue.
A gain of lower than 1 is not expected, and implausible, as this signifies the subject was oscillating more during the calibration segment compared to the fixation segment. The error may be explained due to noisy measurements and observed drift in the readings as the test progressed. However, the testing process can still be considered reasonable and valid as it revealed subjects with distinctly high gains - those who could potentially be strabismic.

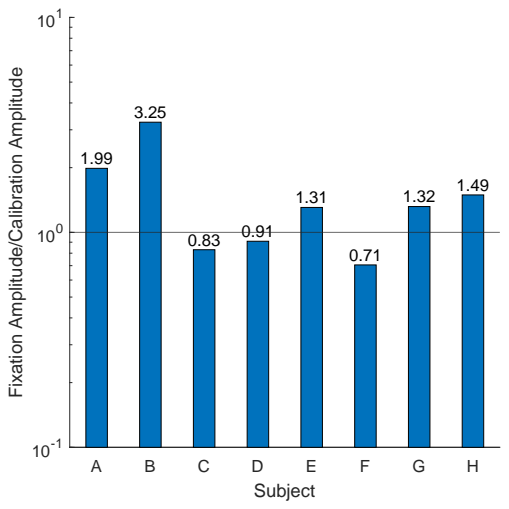
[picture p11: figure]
Subject

Fixation Amplitude/Calibration Amplitude

(a)

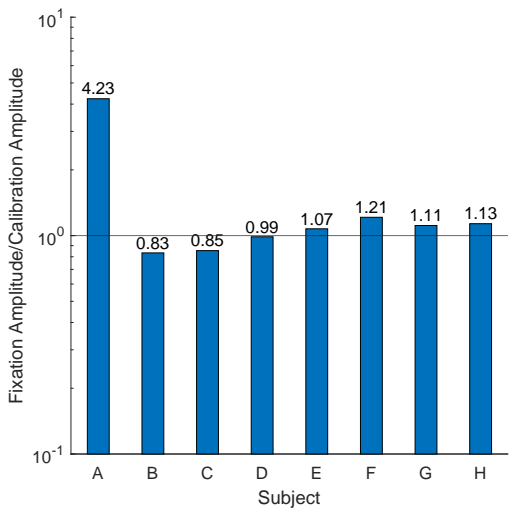
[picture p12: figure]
Subject

Fixation Amplitude/Calibration Amplitude

(b)

Figure 10 Fixation amplitude at 1 Hz over calibration amplitude at 1 Hz at the bottom-left corner of 9-point grid. a) Relative horizontal gain for all 8 subjects. b) Relative vertical gain for all 8 subjects.

### 5.2 Tracking Test

5.2.1 Subject B Results
The second section of the experiments included the tracking tests. These tracking tests would enable us to analyse the subject’s gain and phase at the 0.12 Hz (frequency of stimulus) in order to determine their tracking performance and whether there are measurable differences between the eyes of subjects to predict strabismus. Similar tracking tests were conducted by Saisara et al. [10], however, they computed the Euclidean distance of the two eyes to predict strabismus rather than conclude the gain and phase in the two eyes. Subject B, another visually normal subject, was chosen to report on for the individual tracking test analyses. The patterns of Subject B’s results suggests that they may have performance differences between the two eyes. In Figure 11, the responses of horizontal and vertical smooth pursuit tasks are shown. For each of these, there is one red filter and one blue filter plot, corresponding to the monocular left and right eye-tracking, respectively.

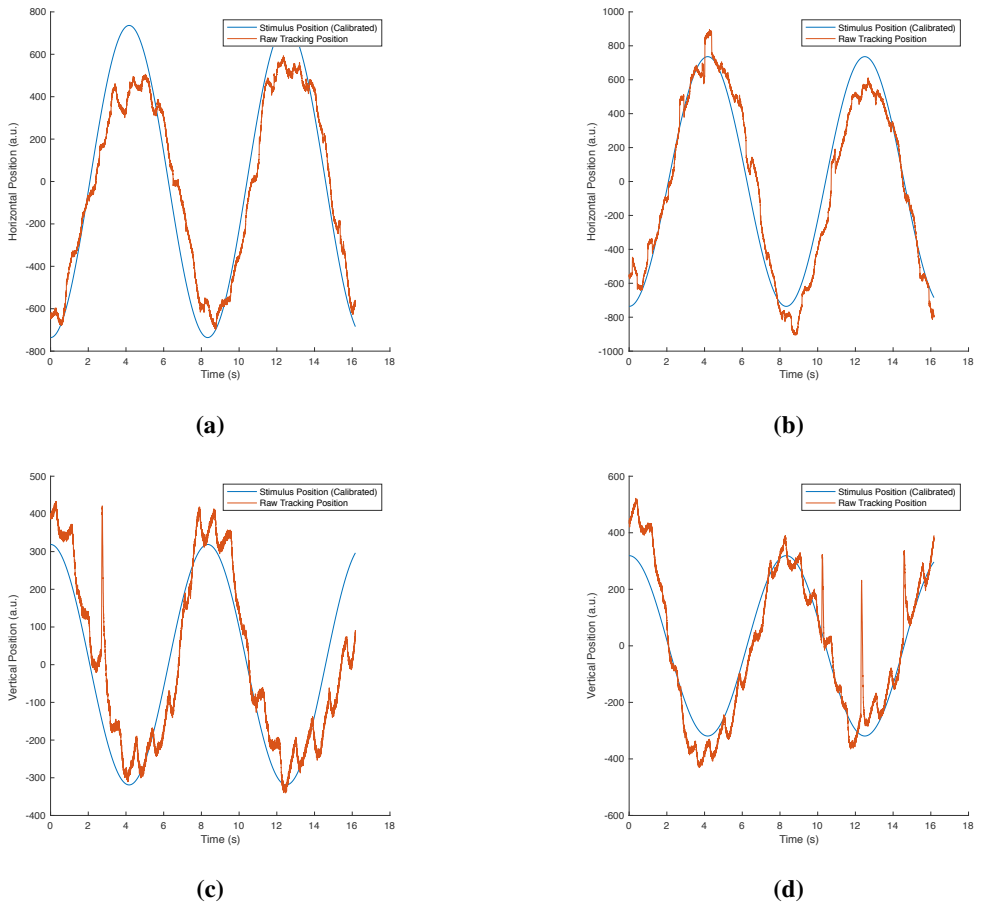
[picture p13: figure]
Time (s); Horizontal Position (a.u.); Stimulus Position (Calibrated) Raw Tracking Position; Vertical Position (a.u.)

Figure 11 Subject B tracking test response with filter placement RB. a) Horizontal tracking with left eye.
b) Horizontal tracking with right eye. c) Vertical tracking with left eye. d) Vertical tracking with right eye.

Table 2 Subject B Gain and Phase at 0.12 Hz component
| Horizontal | Vertical
Left Eye | Right Eye | Left Eye | Right Eye
Gain | 0.7695 | 0.9392 | 0.9486 | 1.1004
Phase (rads) | 0.4101 | 0.3353 | 0.5533 | 0.2444

It can be observed from the plots and table above, Table 2, that the 0.12 Hz gain is generally larger for the right eye (blue) compared to the left eye. This suggests that when tracking with the right eye, Subject B may have better tracking performance with the right eye than the left. Tracking with the left eye may result in an undershoot. These undershoots (or overshoots) illustrate while the subject was tracking monocularly, the resultant gaze position of both eyes were further in (or further out) than where the stimulus was presented.
The phase from the tracking analyses reveal the lag (in radians) behind the stimulus. Although all quantities have some lag, the plot allows us to see if there have been any anticipation or ‘forward thinking’ by the subject throughout the test. For example, this is apparent in Figure 11d, as Subject B was reaching the first trough. In general, Subject B’s right eye had a gain closer to 1 and showed lower phase lag which indicate the ocular dominance of right eye over left eye. We expect to see similar or greater ocular dominance in strabismic patients, via their differences in gain and phase between the two eyes.

5.2.2 Group Results
Strabismic subjects often suppress images from the deviated eye when viewing binocularly. Due to their seldom use of the deviated eye, tracking performance is significantly poorer in the deviated eye [17]. This tracking test enables the use of both eyes monocularly so the performance of dominant eye (DE) and non-dominant eye (NDE) can be visualised. Figures 12 and 13 display both DE, NDE, and the difference between the two, for horizontal and vertical tracking. The difference between DE and NDE is represented as the absolute difference in gain and phase - as it was not possible to show a negative gain in a polar coordinate system. Only the first quadrant is shown in the figures because all test subjects had minimal phase lag. If a strabismic (or other) subject were to show large phase lag (or had phase lead), the quadrant could be extended to the full 360° plot.
Displayed below are all 8 subjects from the formal trials and their respective DE or NDE plots. In horizontal tracking, Figure 12, all but one were fairly consistent between both their tracking tests. Subject F had a larger gain with their NDE and larger phase with their DE hence, the third plot shows this as an outlier. Similar cases were seen in the vertical tracking, Figure 13, where Subjects G and H had vastly larger gains from their NDE. These larger gains observed in the NDE may express the fact that the eye is under-utilised, and could be potential characteristics of strabismus.

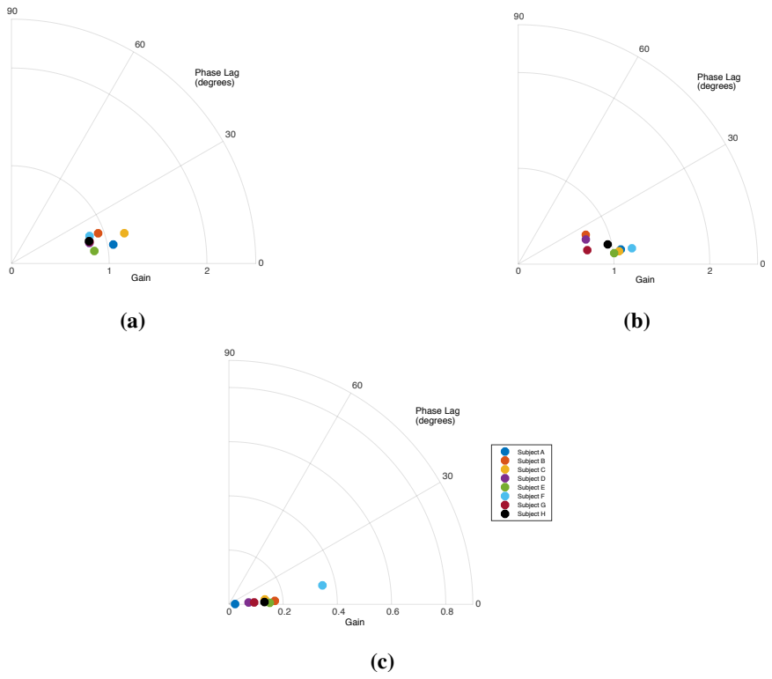
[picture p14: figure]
Gain; Phase Lag (degrees); Gain (b); Subject A Subject B Subject C Subject D Subject E Subject F Subject G Subject H

Figure 12 Polar plot of gain and phase for horizontal tracking. a) Dominant eye tracking. b) Non-dominant eye tracking. c) Difference between dominant and non-dominant eye.

### 5.3 Accuracy of Results

Of the series of tests explained formerly, a major setback for the results displayed in this section is the lack of comparison with a known strabismic subject. Both the fixation and tracking test are able to distinguish common characteristics exhibited by a strabismic patient - such as large magnitude oscillations, large relative gain between oscillation and

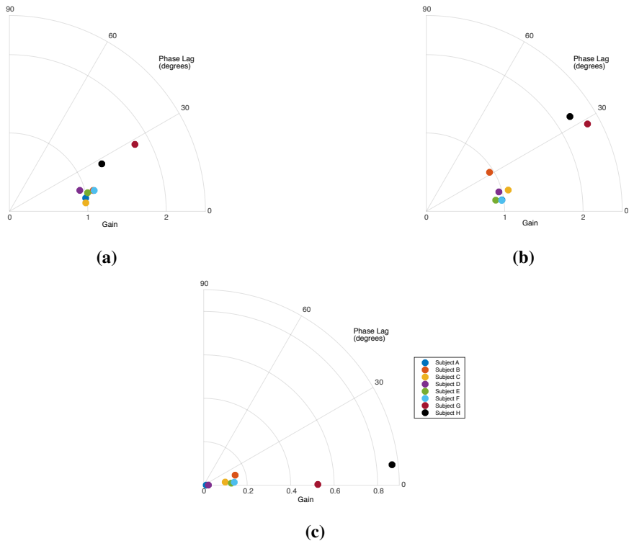
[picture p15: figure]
Phase Lag (degrees); Gain (a); Gain (b); Subject A Subject B Subject C Subject D Subject E Subject F Subject G Subject H; Gain (c)

Figure 13 Polar plot of gain and phase for vertical tracking. a) Dominant eye tracking. b) Non-dominant eye tracking. c) Difference between dominant and non-dominant eye.

non-oscillation, under/over-shoot in resultant gaze position, and large gain/phase in NDEs. Another point to note is that the Jazz-novo eye-tracker data was quite easily affected by noise, and had varying drift (especially in vertical axis) if not worn precisely, hence a slight skew in Figure 8a could be noticed. Therefore, not all data shown may be as accurate as analysed, however, control actions were taken to disregard outliers and anomalies as much as possible. Multiple test trials with one subject could be tried in the future to validate the measurements and analyses presented here. Despite the setbacks, the tests presented valid hypotheses in diagnosing a strabismic subject, so the concept of the tests remain valid. A more accurate, and possibly less invasive, eye-tracker could have provided with cleaner results and findings.

### 6. Conclusion

In this research, we aimed to design, build and test an eye-tracking system for the diagnosis of visual deficits. The central theme revolved around strabismic patients who may require early intervention to prevent further visual deficits, as well as psychosocial issues.
The designed system implemented two forms of testing procedures; the fixation test and the tracking test. The fixation test enabled the analysis of a subject’s gaze point in the nine different directions of the grid. The tracking test enabled the analysis and smooth pursuit performance of the two individual eyes. The testing was possible due to the phenomenon of dichoptic presentation with the use of red & blue dichroic filters and coloured stimuli. The results from the set of trials, with the eight volunteer subjects, revealed the following characteristics from the test, most likely required for diagnosing strabismus:

- Magnitude of oscillations at the 1 Hz frequency component in all 9 gaze directions
- Amount of deviation in individual eye when fixating compared to alternating
- Identifying the deviated eye via under/over-shoots in gaze response in smooth pursuit
- Using difference between DE and NDE gains and phase to illustrate tracking performance

Currently, the results are based off visually normal subjects but further testing with a strabismic patient group could see validation of these results and confirmation of successful diagnosis of strabismus.

### 7. Future Work

Following the conclusion of this project, some key areas of the research as well as the experimental trials were identified for further development. These are outlined below. Further testing of subjects. As the principal goal for this research, testing of strabismic patients would be required to conclude the validity of our eye-tracking system as a diagnostic tool for strabismus. Similarly, further testing of visually normal subjects would also be key into recognising patterns such as those observed in this group of subjects. Automated analysis via Machine Learning. With enough subject data, pattern recognition could be utilised for learning algorithms. These algorithms would help further automate the entire process making it faster and more efficient, and would also allow more accurate, and objective classifications of subjects.
Less invasive methods. Early intervention of strabismus in children and infants is vital. However, the current eye-tracking method may be unsuitable for many children to use. A more accurate and non-invasive eye-tracking device would be required for use on young children such that the device would not introduce any bias during testing from experiencing discomfort.
Mobile system. Utilising the high resolution cameras in tablet and other devices can allow for a mobile system. Having a mobile system would enable a non-invasive screening process and enable high throughput in clinical environments for both patients and clinicians.

### References

[1] M. Castanes, “Major review: The underutilization of vision screening (for amblyopia, optical anomalies and strabismus) among preschool age children.” Binocular vision & strabismus quarterly, vol. 18, no. 4, pp. 217–232, 2003.
[2] J. M. Durnian, C. P. Noonan, and I. B. Marsh, “The psychosocial effects of adult strabismus: a review,” British Journal of Ophthalmology, vol. 95, no. 4, pp. 450–453, 2011. [Online]. Available: https://bjo.bmj.com/content/95/4/450

[3] S. P. Donahue and C. N. Baker, “Visual system assessment in infants, children, and young adults by pediatricians,” Pediatrics, vol. 137, no. 1, pp. 28–30, 2016.
[4] M. Horsley, M. Eliot, B. A. Knight, and R. Reilly, Current trends in eye tracking research. Springer, 2013.
[5] Z. H. Chen, H. Fu, W. L. Lo, Z. Chi, and B. Xu, “Eye-tracking-aided digital system for strabismus diagnosis,” Healthcare technology letters, vol. 5, no. 1, pp. 1–6, 2018.
[6] G. K. Von Noorden and E. C. Campos, Binocular Vision and Ocular Motility: Theory
and Management of Strabismus. Mosby St. Louis, 2002, vol. 6.
[7] J. R. Economides, D. L. Adams, and J. C. Horton, “Perception via the deviated eye in strabismus,” Journal of Neuroscience, vol. 32, no. 30, pp. 10 286–10 295, 2012.
[8] K. Harezlak and P. Kasprowski, “Application of eye tracking in medicine: A survey, research issues and challenges,” Computerized Medical Imaging and Graphics, vol. 65, pp. 176–190, 2018.
[9] Z. M. Hafed, K. Stingl, K.-U. Bartz-Schmidt, F. Gekeler, and E. Zrenner, “Oculomotor behavior of blind patients seeing with a subretinal visual implant,” Vision research, vol. 118, pp. 119–131, 2016.
[10] U. Saisara, P. Boonbrahm, and A. Chaiwiriya, “Strabismus screening by eye tracker
and games,” in 2017 14th International Joint Conference on Computer Science and Software Engineering (JCSSE). IEEE, 2017, pp. 1–5.
[11] Tobii Gaming, “Tobii eye tracker 4c,” [Online]. Available: https://gaming.tobii.com/product/tobii-eye-tracker-4c/, (https://gaming.tobii.com/product/tobii-eye-tracker-4c/) 2019, [Accessed 3-May-2019].
[12] Tobii AB, “Eye tracking as a diagnosis tool for eye movement disorders - a look at nystagmus,” [Online]. Available: http://www.ober-consulting.com/page/opis_jazz/, 2019, [Accessed 3-May-2019].
[13] Ober Consulting, “Jazz-novo multisensor,” [Online]. Available: https://www.tobiipro.com/fields-of-use/clinical-research/case/university-melbourne/, (https://www.tobiipro.com/fields-of-use/clinical-research/case/university-melbourne/) [Accessed 3-May-2019].
[14] R. Honsbeek, T. Kuiper, and C. M. van Rijn, “Biosemi,” [Online]. Available: https: //www.biosemi.com/, [Accessed 3-July-2019].
[15] M. Kleiner, D. Brainard, D. Pelli, and T. Wolf, “Psychtoolbox-3,” [Online]. Available: http://psychtoolbox.org/, [Accessed 3-July-2019].
[16] R. Oostenveld and J.-M. Schoffelen, “Fieldtrip,” [Online]. Available: http://www.fieldtriptoolbox.org/, [Accessed 3-July-2019].
[17] M. J. Mustari and S. Ono, “Neural mechanisms for smooth pursuit in strabismus,”
Annals of the New York Academy of Sciences, vol. 1233, no. 1, pp. 187–193, 2011.

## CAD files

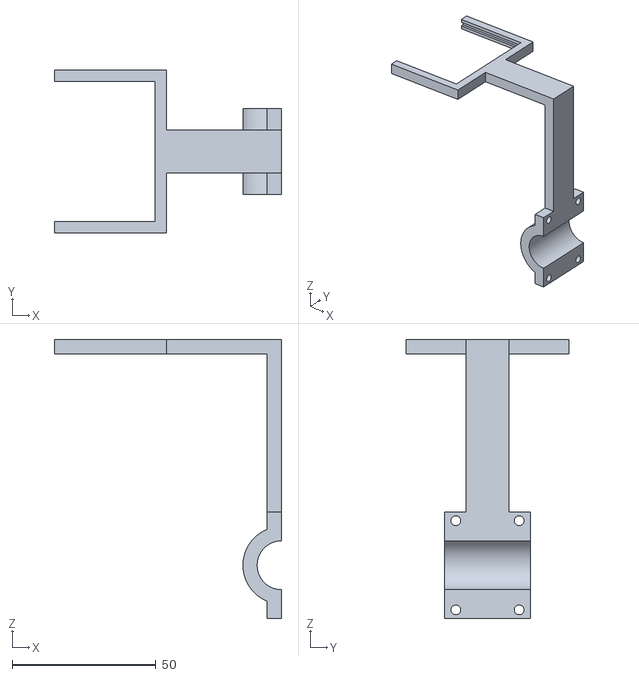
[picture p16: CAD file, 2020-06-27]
Filter Mounts/filterlensemount3.stl
79.0 x 56.5 x 97.0

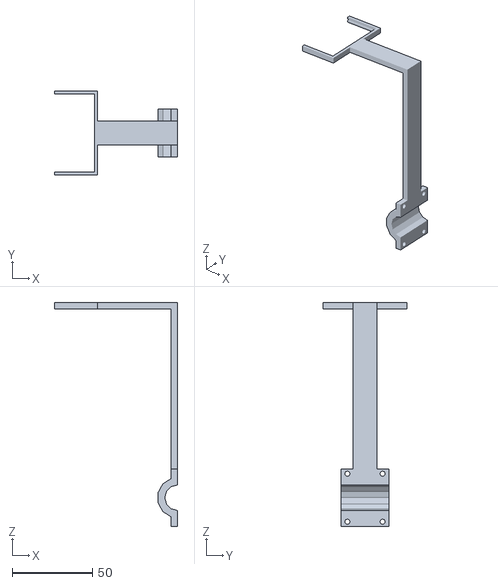
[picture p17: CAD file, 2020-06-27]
Filter Mounts/filterlensemount.stl
77.0 x 52.5 x 140.0

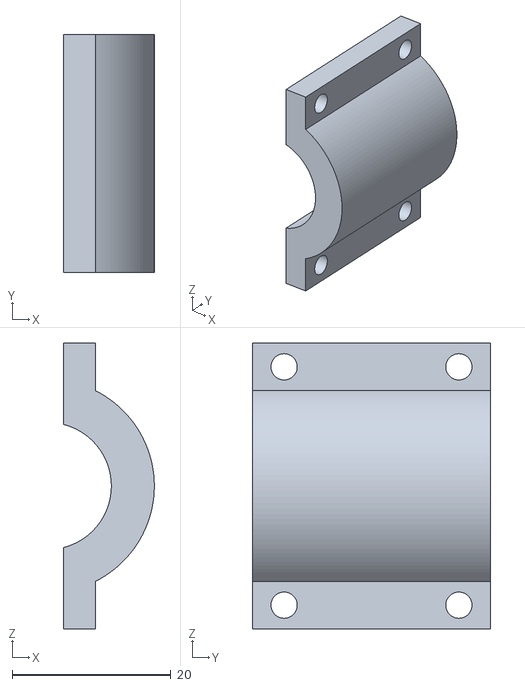
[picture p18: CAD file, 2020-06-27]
Filter Mounts/filterlenses_screwmount2.stl
11.4 x 30.0 x 36.0

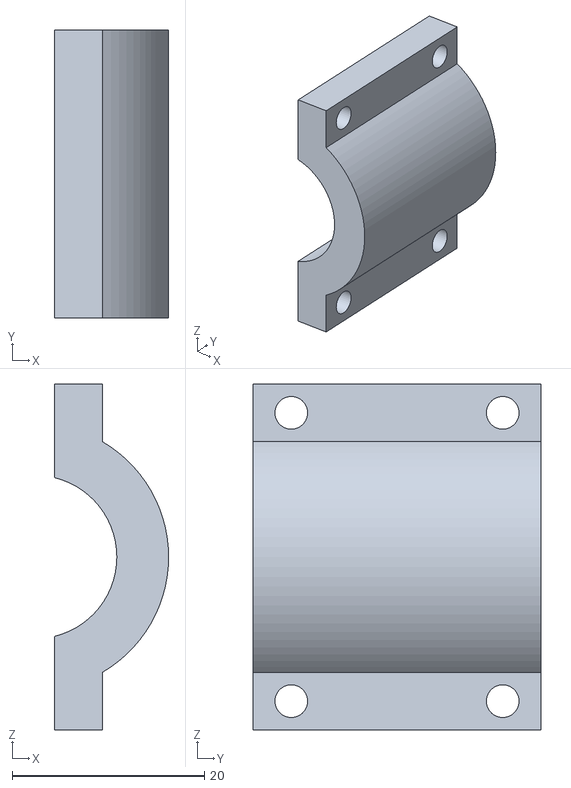
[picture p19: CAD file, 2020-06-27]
Filter Mounts/filterlenses_screwmount3.stl
11.9 x 30.0 x 36.0

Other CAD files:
Filter Mounts/filterlensemount2.stl

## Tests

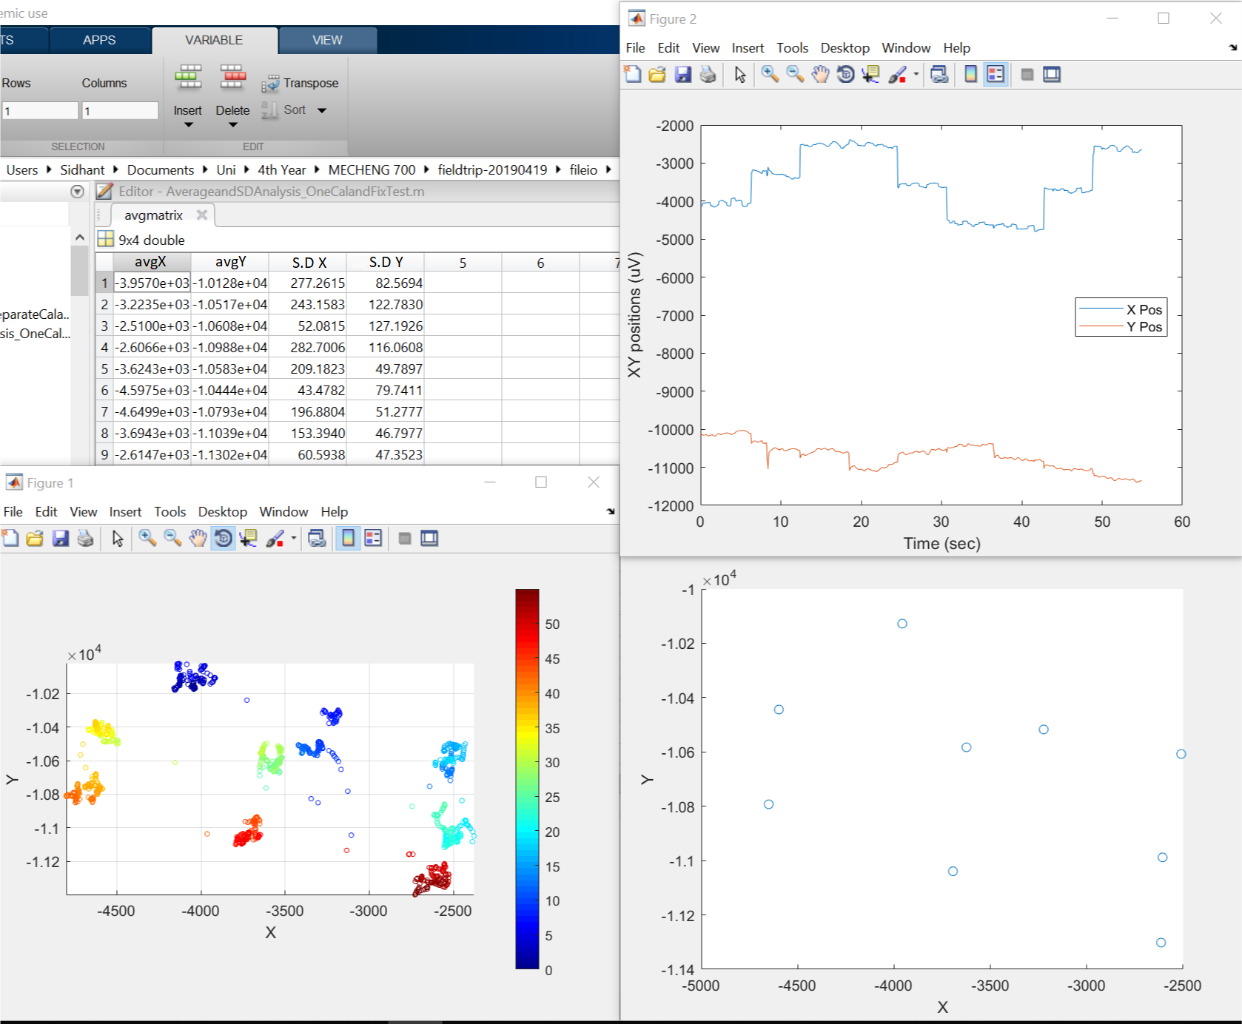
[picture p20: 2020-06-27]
Test Subjects/Test data Images/Show Luke 2407/FixationTestwithAnalysis_Sid2307.png

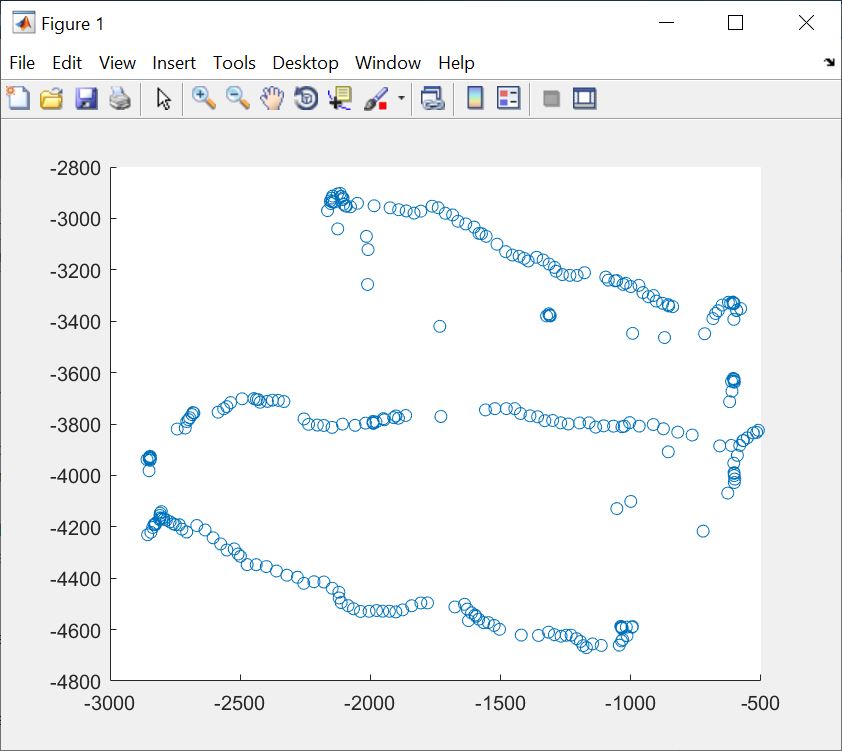
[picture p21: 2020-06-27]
Test Subjects/Test data Images/TrackingTestdata_HorizontalRed_Sid2207.JPG

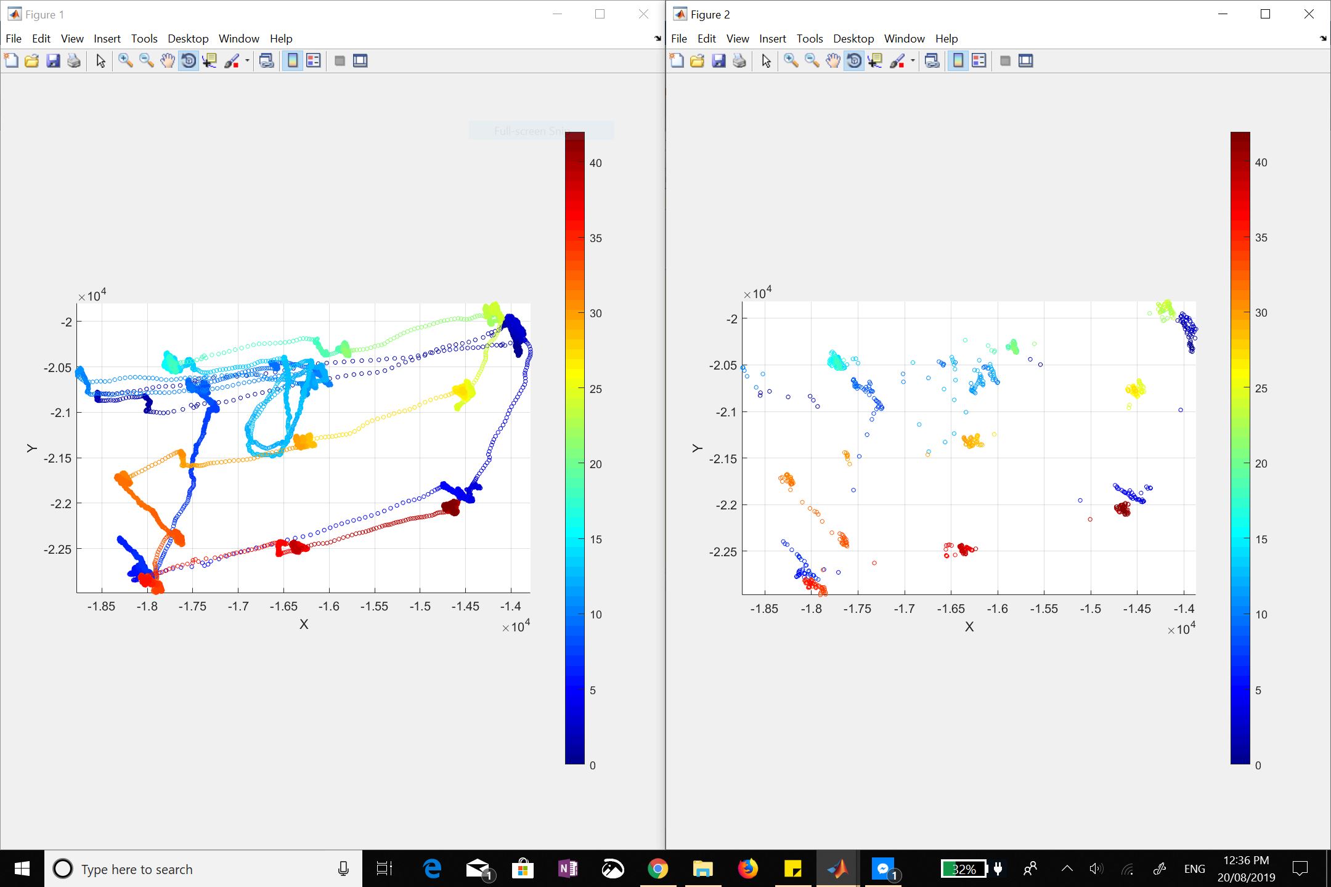
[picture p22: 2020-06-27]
Test Subjects/Test data Images/Michael_Fixation.JPG

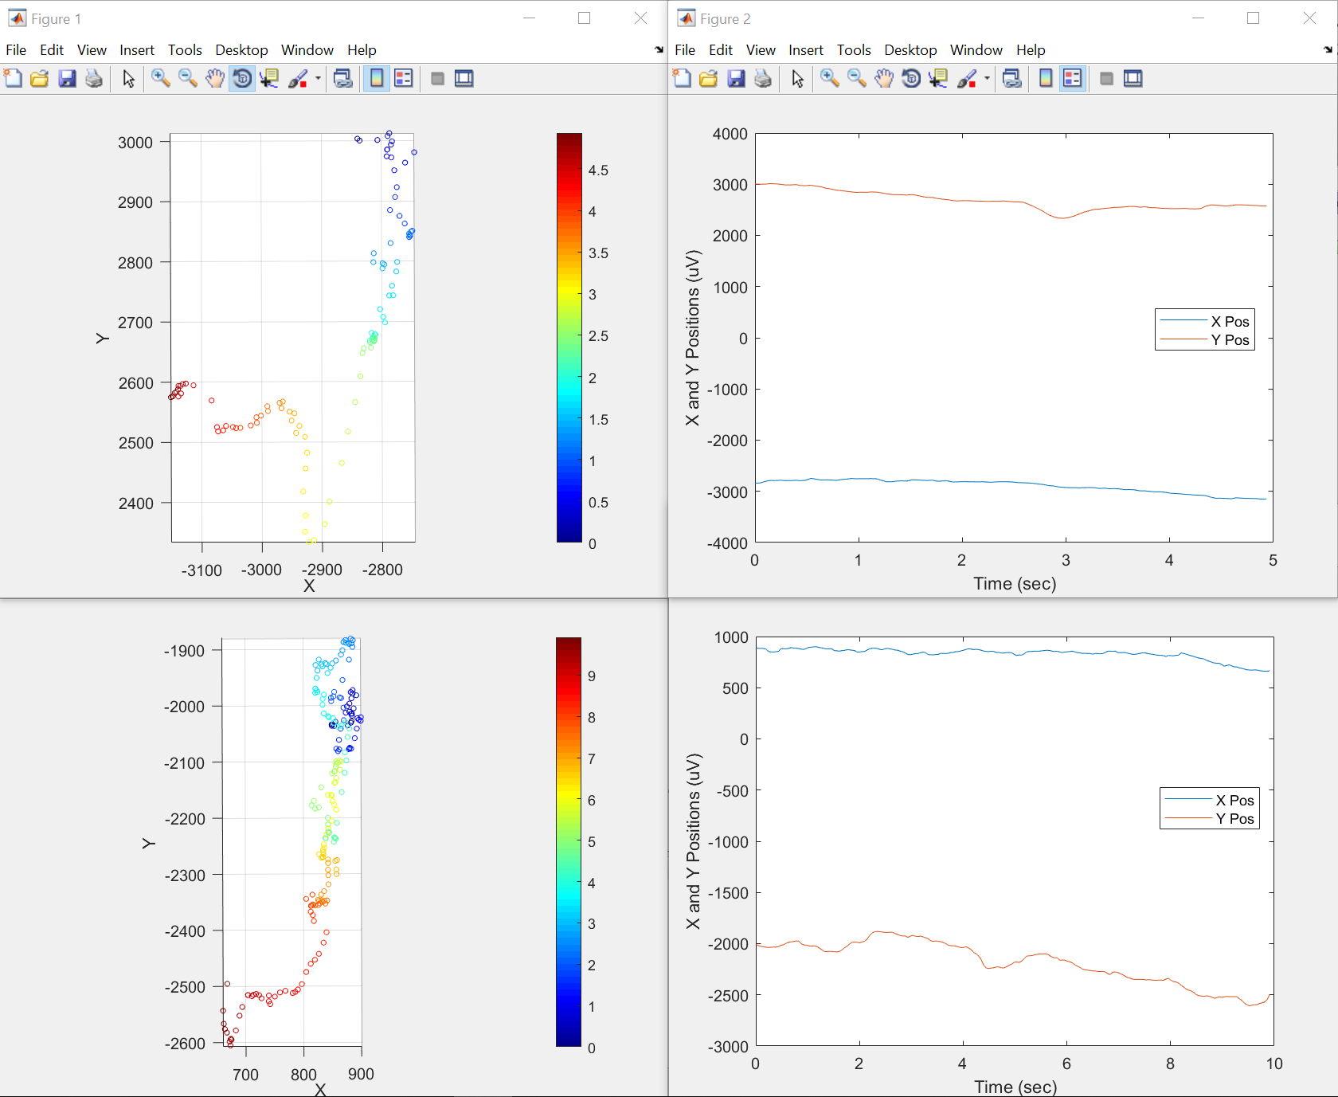
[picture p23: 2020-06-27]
Test Subjects/Test data Images/Show Luke 2407/CalibrationAndOscillationTest_Sid2407.png

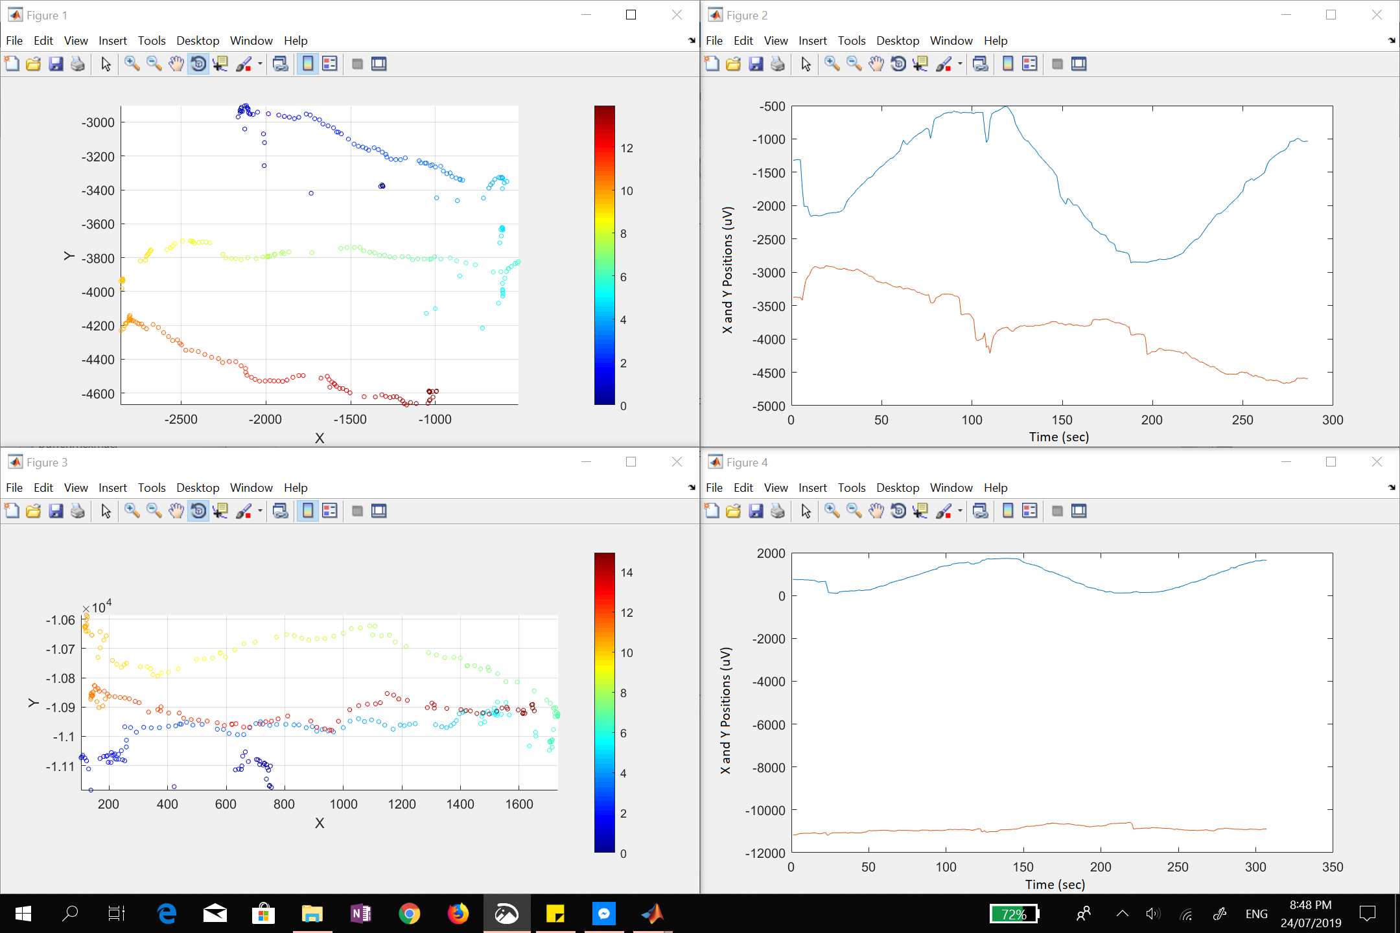
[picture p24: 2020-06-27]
Test Subjects/Test data Images/Show Luke 2407/TrackingTestdata_HorizontalRed_Sid2207_1and2.png

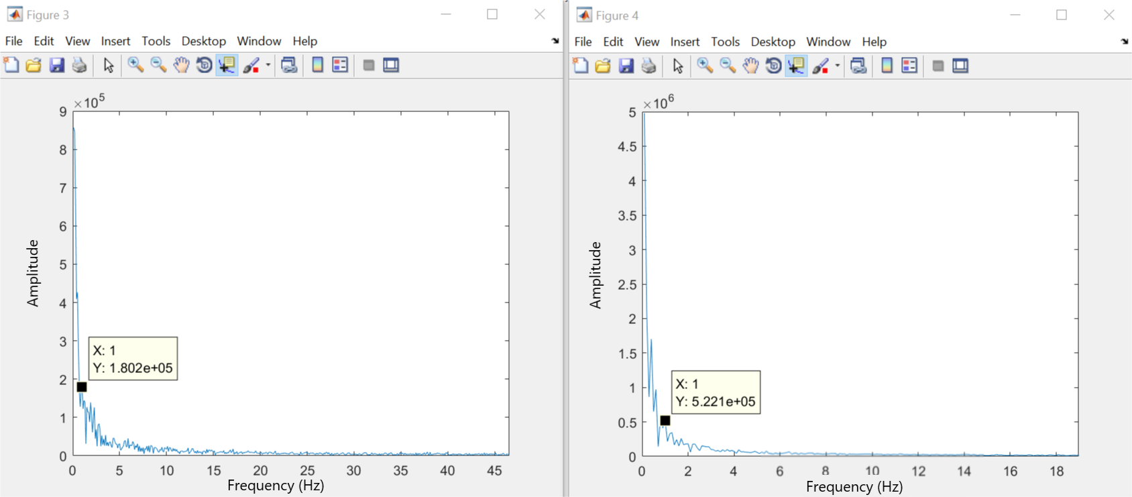
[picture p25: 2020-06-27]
Test Subjects/Test data Images/Show Luke 2407/FourierAnalysis_CalibrationTest_Sid2407.png

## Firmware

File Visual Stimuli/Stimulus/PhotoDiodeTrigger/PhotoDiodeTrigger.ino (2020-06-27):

int led = 13;
int gtec = 8;


 void setup() {
  pinMode(led, OUTPUT); 
  pinMode(gtec, OUTPUT);
  int digitalwrite(led,LOW);
  Serial.begin(9600);
}

 void loop() {
  int sensorValue = 0;
  sensorValue = analogRead(A0);
  Serial.println(sensorValue);
  if (sensorValue>600)
  {
    digitalWrite(led,HIGH);
    digitalWrite(gtec,HIGH);
//    Serial.println("trigger");
  } 
  else {
    digitalWrite(led,LOW);
    digitalWrite(gtec,LOW);
  }

}
